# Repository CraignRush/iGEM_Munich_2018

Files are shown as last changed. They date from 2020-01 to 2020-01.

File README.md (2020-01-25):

# iGEM Munich 2018 Repository
This is an additional repository for many files which were created during the 2018 iGEM Munich season. It consists of three parts:
- _PhageCAD:_ Some CAD files to 3D-Print phage models
- _DropletVaporizer:_ CAD files to build an easy droplet vaporizer to produce alginate beads (in our case with phages in it) via 3D-printing
- _Model:_ Some parts of the iGEM Munich 2018 model. A simulation, how phages would reproduce inside a cell with respect to degradation an other intrinsic processes

## PhageCAD

The phage model looks like this:
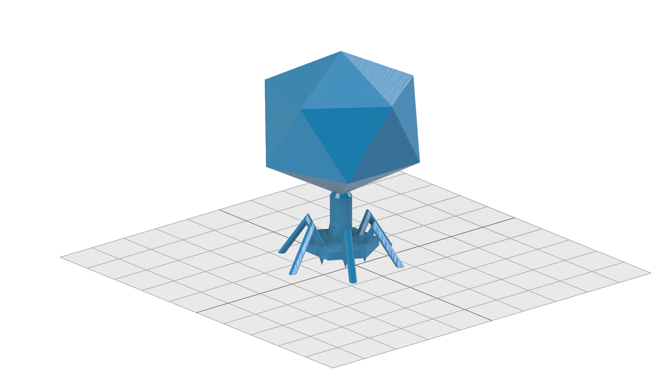
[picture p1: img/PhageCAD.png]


## Droplet Vaporizer
### Introduction

Phactory yields phages with toxicity levels that allow for oral administration to the patient. However, oral delivery requires protection of the phages from rapid degradation in the acidic gastric juice, while direct intravenous application requires additional purification steps. To overcome these hurdles, we prototyped two 3D-printed fluidic devices that each can be assembled for less than $5.

For oral application, we built the Phagecapsulator, a nozzle to encapsulate the phages in monodisperse calcium-alginate microspheres that protect them in the stomach. For intravenous administration, we can purify the bacteriophages from the remaining cell-extract via fractionation in a pressure-driven size-exclusion Phactory-Purificator filter system.

### Phage-Encapsulator
#### Motivation

As in many manufacturing processes, packaging of our produced phages is the final step of Phactory. Packaging provides long-term storability and ensures a clean and safe product for patients. Lacking access to commercial bioencapsulation devices such as the Inotech Encapsulator IER-50, available at $10,000, we engineered Phage-Encapsulator, an affordable device for encapsulating phages in monodisperse alginate spheres (1).

Requiring only standard parts, phage solution, alginate and compressed air, Phage-Encapsulator makes phage packaging accessible to non-specialized laboratories. The throughput is sufficient to produce encapsulated phages for oral application on-site in less than 2 hours.
Overall design

The core part of the Phage-Encapsulator consists of a dispensing tip that is continuously fed with phage containing alginate solution by a syringe pump. The dispensing tip is surrounded by a chamber connected to a compressed air supply to create a steady stream of air around the tip that shears off a jet of monodisperse droplets, smaller than the diameter of the tip. The alginate droplets are sprayed into a Calcium-Chloride bath where the rapid crosslinking reaction occurs.

<p align="center">
  A generic square placeholder image with ounded corners in a figure. 
  A generic square placeholder image with rounded corners in a figure.
 
</p>

#### Individual Parts:
##### Alginate Solution

The negatively charged polysaccharide alginate is commonly used for cell encapsulation or as food additive. Alginate undergoes strong shrinking when the pH of the environment drops below its pKa (2). Due to its pKa of ~3.5 this is the case in gastric fluid with a pH of 1 – 2. These properties render alginate spheres an ideal delivery substrate, protecting the phages in the stomach and releasing them in the basic milieu of the intestinal tract. As a tradeoff between alginate viscosity and gel strength, we found that a mixture of 1.8% high viscosity alginate (Art.-No. 9180.1, ROTH) and 0.2 low viscosity alginate (A1112, Sigma Aldrich) represents a good compromise.

##### Nozzle
Our final design of the nozzle is shown in Interactive Figure 1. It consists of a chamber that can be connected to a pressure supply via a universial tube adapter. Consisting of two parts, the nozzle does not get in contact with the phage solution, so it can be reused. The dispensing tip can be easily inserted via a Luer-lock adapter and lines up precisely with the nozzle orifice. A centering aid is located behind the orifice to reduce variances in cannula alignment, while the air stream is not disturbed unequally by its symmetric shape. At a given air pressure, the orifice diameter determines the velocity of the air stream and consequently the droplet diameter.

##### Calcium bath
Rapid gelation of the phage-containing alginate droplets was obtained in a 10 mM MgSO4 solution with 1.8% CaCl2. Aggregation of alginate droplets was prevented by continuous stirring during droplet generation with a magnet stirrer.

##### Syringe pump
In our experiments we used a commercial syringe pump from TSE Systems (type 540060) to create a continuous alginate stream. We designed our nozzle to be compatible with other types of syringe pumps, including open-source solutions.

##### Pressure supply
As a pressure supply we used the house gas line, reduced to 1 bar. If not available, the universial tube adapter ensures compatibility to alternative pressure supplies, including portable, open-source solutions.
Part List

- syringe (1ml Braun Omnifix)
- dispensing Tip (ID 0.51mm, Vieweg)
- syringe pump
- pressure supply
- pneumatic tubing
- 4x M3x20 screws + nuts
- 3D printed nozzle (PMMA)

#### Results

Our results show that after 1 hour incubation in simulated gastric fluid, active phages are successfully released in simulated intestinal fluid. Within the limited time frame of the iGEM competition we were able to show storability of these alginate spheres with constant phage activity at 4°C for four weeks, while stability for several months was shown in the literature (3).

##### Droplets are Monodisperse
<p align="center">
  
  <br>
  <p align="center">
    Alginate composition of 1.8 % Alginate and<br>0.2 % low-viscosity Alginate delivers<br>spherical Alginate microspheres.
  </p>
</p>
<br>
<p align="center">
  
  <br>
  <p align="center"  width="40%">
    Alginate encapsulated phages, DNA stained with SYBR Gold.
  </p>
</p> 
In order to achieve defined phage concentrations and therefore defined doses, we optimized the monodispersity of our alginate droplets.

In our initial attempts to create alginate droplets the size within a batch often varied significantly. Additionally, due to aggregation a lot of droplets were lost. Optimization of parameters such as flow rate, alginate concentration and N2 pressure led to an increase of monodispersity for all tested sizes (50-300 μm). Specifically, an alginate concentration of 1.8 % alginate and 0.2 % low-viscosity alginate proved to be ideal. Pressure and flow rate determine the droplet sizes.
<p align="center">

 <br>
 <p align="center">Monodispersity of alginate droplets with three different diameters<br>before and after optimization of the hardware device.</p>
 </p>

##### Bacteriophages Encapsulated In Alginate Can Withstand Gastric Acid 

The main problem of oral application is the acidic environment in the gastric fluid, necessitating protective measures against degradation. The other requirement of phage protection is the release of functional phages in the intestines. For this reason we compared the behavior of the encapsulated phages and non-encapsulated phages in simulated gastric fluid (SGF) and simulated intenstinal fluid (SIF).

In SGF, the number of active non-encapsulated phages decreases by more than 99.99 % within an hour. This shows the urgent need of a form of protection against degradation to make oral application of bacteriophages possible. As a reference, we used phages that were chemically released by citrate from alginate droplets.
<p align="center">

 <br>
 <p align="center">Non-encapsulated phages are highly degraded<br>within an hour in simulated gastric fluid.</p>
</p>

In comparison, the encapsulated phages were tested in SGF for the same time as the non-encapsulated phages. Afterwards, the same droplets were exposed for two hours to simulated intestinal fluid to test the release of functional bacteriophages in this environment.

The encapsulated phages were barely released in an hour of exposure to SGF. After transfering the capsules to SIF the number of active phages reached that of the undegraded reference. This indicates that the encapsulation of bacteriophages in alginate capsules enables the possibility of an oral application. Further experiments could test the alginate capsules in an animal model system.
<p  align="center">

 <br>
 <p align="center" >A small amount of encapsulated phages are released in SGF.<br> In SIF, functional phages are released in high concentration.</p>
 </p>

### References
<ol>
<li> <a href=https://doi.org/10.1016/j.biomaterials.2009.07.034>Chan, A. W., &amp; Neufeld, R. J. (2009). Modeling the controllable pH-responsive swelling and pore size of networked alginate based biomaterials. Biomaterials, 30(30), 6119–6129. </a></li>
<li> <a href=https://doi.org/10.1016/j.ab.2007.10.045>Kwon, Y.-C., Hahn, G.-H., Huh, K. M., &amp; Kim, D.-M. (2008). Synthesis of functional proteins using Escherichia coli extract entrapped in calcium alginate microbeads. Analytical Biochemistry, 373(2), 192–196. </a></li>
<li> <a href=https://doi.org/10.1038/srep41441>Colom, J., Cano-Sarabia, M., Otero, J., Aríñez-Soriano, J., Cortés, P., Maspoch, D., &amp; Llagostera, M. (2017). Microencapsulation with alginate/CaCO3: A strategy for improved phage therapy. Scientific Reports, 7(1). </a></li>
</ol>

## Model

Visit this page for more information regarding the model.
### Cell-free Biosynthesis of Bacteriophages

The seemingly simple experimental procedures of the optimized framework of Phactory may lead to the false impression that cell-free biosynthesis of bacteriophages is a trivial process. In fact, the production of phages represents one of the most complicated self-assembly processes that have been realized in a synthetic context.

We chose the T7 phage as a model system for cell-free phage production, because it is well characterized in the literature and our experiments. The phage assembly reaction resembles a temporally orchestrated process, which involves the expression of more than 40 proteins. This genetic program, encoded by the phage genome, is executed in a test tube containing hundreds of proteins, ribosomes, tRNAs and small molecules.

Due to the complexity of this process, variations in the quality of our cell extract cause irreproducible results. To optimize bacteriophage titers, we created a model based on ordinary differential equations to understand the essential features of a phage assembly reaction in a quantitative manner.

### Assumptions and Parameter Estimation

A phage assembly reaction follows a temporal program (1). First, the genes controlled by E. coli promoters, including the T7 DNA and RNA polymerase are expressed. Once the T7 RNA polymerase is present, the transcription of genes under a T7 promoter, e.g. the capsid proteins, starts. Our experiments revealed that simultaneously the phage genome being is replicated by the T7 DNA polymerase. As soon as a sufficient amount of capsid proteins is produced, they self-assemble to form empty phage capsids. In a final step the phage genome is packed into the empty capsids forming functional phages. In the following paragraphs we develop a set of ordinary differential equations that describe the phage assembly reaction, give analytical results where appropriate and estimate realistic reaction rate constants.

The modelled properties can be shown by the following tree diagram:


The complete set of model equations is shown below. 
#### Reaction Fluxes
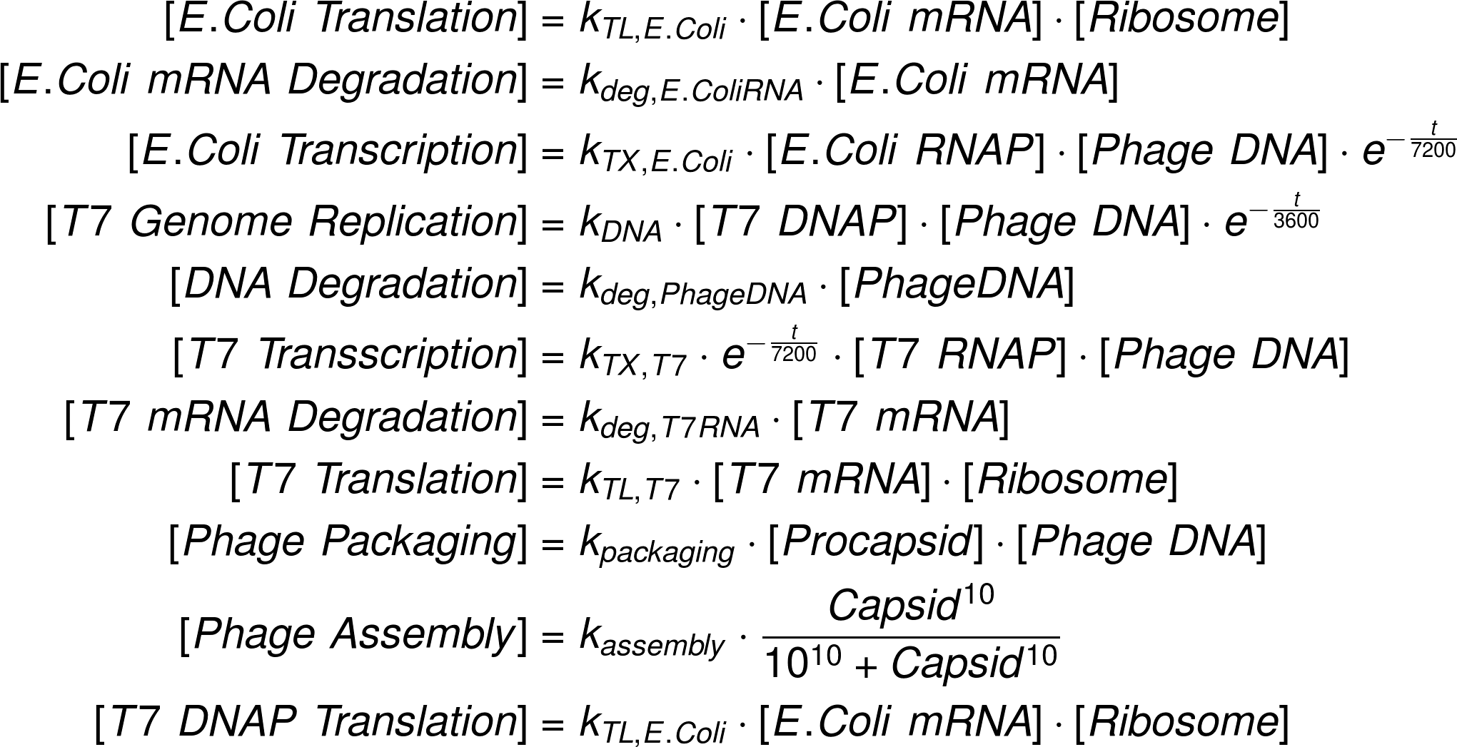
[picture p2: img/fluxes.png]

#### Ordinary Differential Equation System
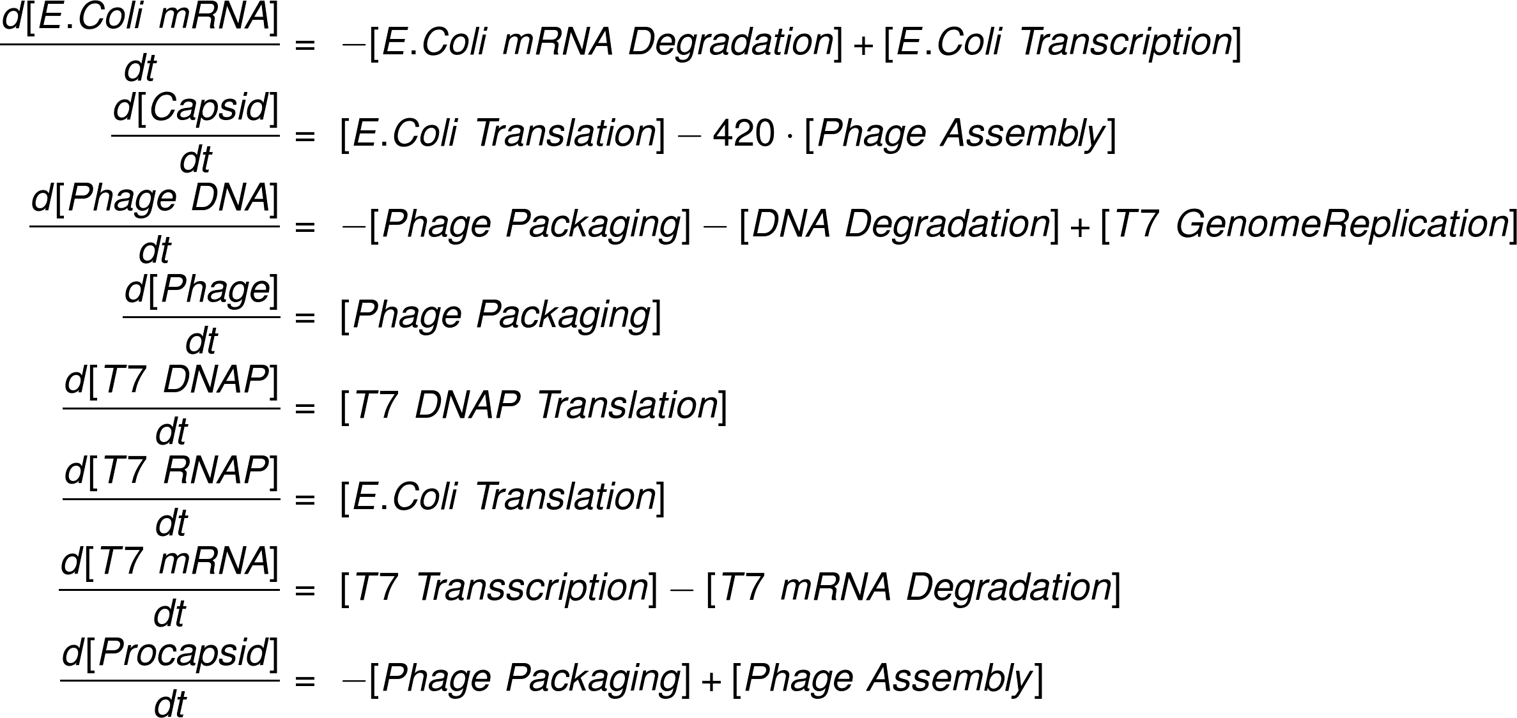
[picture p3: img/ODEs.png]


### Results

We used the MATLAB SimBiology toolbox to analyze the reactions numerically.

#### Phage Assembly Follows a Temporal Program

Evaluating our ODE model we can now follow the time traces of each reaction species in our system. Looking at the mRNA levels, it becomes evident that mRNA transcribed by E. coli RNA polymerase is produced instantly and rapidly reaches a low steady-state level. mRNA transcribed by the T7 RNA polymerase is produced after a time delay and reaches a much higher steady-state level, consistent with the faster transcription rate. Both mRNA levels decrease as the steady state level decreases due to the finite lifetime of the cell extract.

Following protein levels, we see that production of the T7 DNA and RNA polymerases starts first, while production of the T7 RNA polymerase controlled capsid proteins sets in later. When the free capsid proteins exceed the critical concentration __K<sub>c</sub>__ , they start to be assembled into full capsids and the free capsid protein concentration approaches a steady-state. All protein levels approach a final level at the end of the reaction.
<p align="center">

 <br>
 <p align="center">mRNA levels over time in the cell-extract.<br>before and after optimization of the hardware device.</p>
 </p>

Further, it is instructive to inspect the time traces of free DNA and fully packed active phages. As soon as sufficient T7 DNA polymerase is present, the phage genomes are being amplified to approximately 10 times the initial level. The assembly and packing of functional phages, however, only kicks in after an initial time delay. Importantly, this allows the genome to be freely transcribed and replicated, before the negative feedback introduced by DNA packing, impedes further phage production.
<p align="center">

 <br>
 <p align="center">T7 polymerase generation by the E.coli in-house polymerase</p>
 </p>

<p align="center">

 <br>
 <p align="center">Phage production and DNA levels over time</p>
 </p>

#### DNA Stability

To analyze the influence of DNA stability, we screened a range of DNA degradation rates as shown in the figure on the right. Phages are produced until a critical degradation rate of __&delta;<sub>g,c</sub> &asymp; 2 &sdot; 10<sup>-4</sup>__ is reached. This results in lower concentrations of proteins in downstream reactions and resultingly prohibits the formation of procapsids.
<p align="center">

 <br>
 <p align="center">Influence of DNA degradation on the phage production</p>
 </p>

#### Impact of Positive Feedback via DNA Replication

To evaluate the influence of the positive feedback loop introduced by DNA replication, we conducted experiments with and without addition of dNTPs to the reaction mixture. With our model we can simulate this experiment by setting the DNA replication rate to zero.

The bar plot on the right shows enhanced phage packaging of over one decade by the integrated feedback loop of the T7 DNA polymerase.
 
 <p align="center">

 <br>
 <p align="center">Evaluation of DNA polymerase in the phage production.</p>
 </p>

### Conclusions

Based on the results, we identified that enhancing DNA stability and maximizing protein yield are the most relevant parameters to improve phage titers. After optimizing our protocols accordingly, we reached __10<sup>7</sup>__ phages per __10 µL__ reaction - sufficient to treat up to 10 patients.

### References
<ol>
<li id="ref_1"> <a href=https://pubs.acs.org/doi/abs/10.1021/sb300049p>  Shin, J., Jardine, P., &amp; Noireaux, V. (2012). Genome Replication, Synthesis, and Assembly of the Bacteriophage T7 in a Single Cell-Free Reaction. ACS Synthetic Biology, 1(9), 408–413.</a></li>
<li id="ref_2"> <a href=https://www.jove.com/video/56144/synthesis-infectious-bacteriophages-an-e-coli-based-cell-free>  Rustad, M., Eastlund, A., Marshall, R., Jardine, P., &amp; Noireaux, V. (2017). Synthesis of infectious bacteriophages in an E. coli-based cell-free expression system.
</a></li>
<li id="ref_3"> <a href=https://doi.org/10.1103/PhysRevLett.106.048104>  Karzbrun, E., Shin, J., Bar-Ziv, R. H., &amp; Noireaux, V. (2011). Coarse-grained dynamics of protein synthesis in a cell-free system. Physical Review Letters, 106(4).</a></li>
<li id="ref_4"> <a href=https://doi.org/10.1021/sb400203p>Siegal-Gaskins, D., Tuza, Z. A., Kim, J., Noireaux, V., &amp; Murray, R. M. (2014). Gene Circuit Performance Characterization and Resource Usage in a Cell-Free “Breadboard.” ACS Synthetic Biology, 3(6), 416–425. </a></li>
<li id="ref_5"> <a href=https://doi.org/10.1021/sb400131a>
Sun, Z. Z., Yeung, E., Hayes, C. A., Noireaux, V., &amp; Murray, R. M. (2014). Linear DNA for rapid prototyping of synthetic biological circuits in an Escherichia coli based TX-TL cell-free system. ACS Synthetic Biology, 3(6), 387–397.  </a></li>

<li id="ref_6"> <a href=http://www.jbc.org/content/286/1/234.full>Ionel, A., Velázquez-Muriel, J. A., Luque, D., Cuervo, A., Castón, J. R., Valpuesta, J. M., … Carrascosa, J. L. (2011). Molecular Rearrangements Involved in the Capsid Shell Maturation of Bacteriophage T7. Journal of Biological Chemistry, 286(1), 234–242. </a></li>
<li id="ref_7"> <a href=https://books.google.de/books?hl=de&amp;lr=&amp;id=vgyBJbtNOcoC&amp;oi=fnd&amp;pg=PP1&amp;dq=israelachvili&amp;ots=_PQtchA1Q9&amp;sig=Bw7OdRovpmTt5FKFaZCesKrPM18#v=onepage&amp;q=israelachvili&amp;f=false>Israelachvili, J. N. (2011). Intermolecular and surface forces. Academic press.</a></li>

</ol>

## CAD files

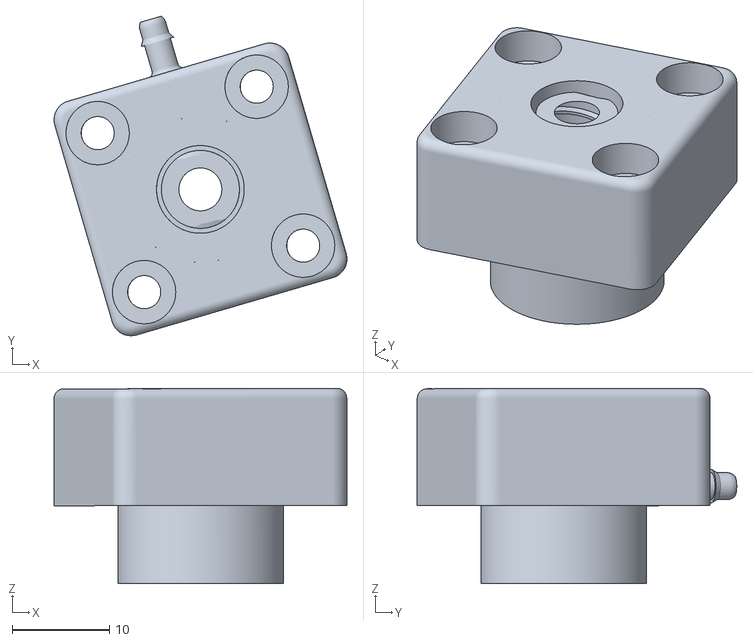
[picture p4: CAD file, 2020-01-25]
DropletVaporizer/Baugruppe_Zerstäuber_Top_V2.stl
30.1 x 32.8 x 20.0

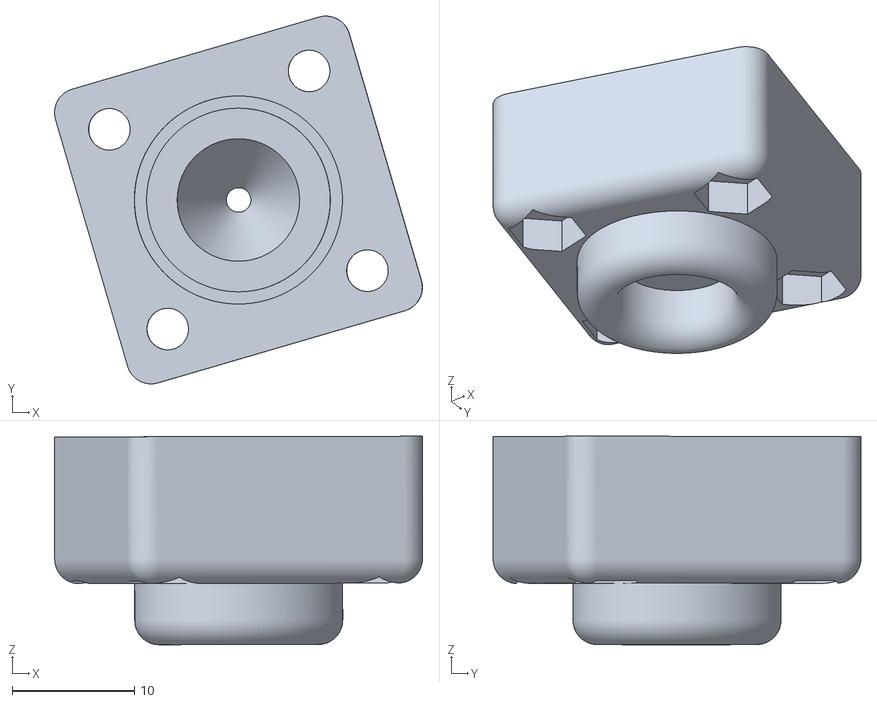
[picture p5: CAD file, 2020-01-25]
DropletVaporizer/Baugruppe_Zerstäuber_Bottom_V2.stl
30.1 x 30.0 x 17.0

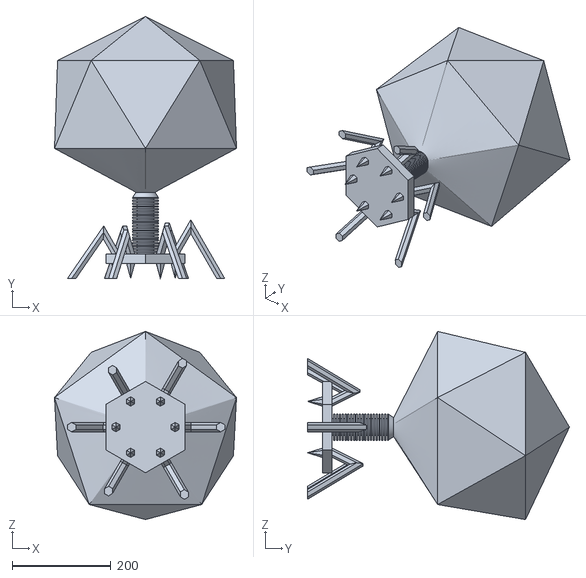
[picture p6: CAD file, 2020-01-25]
PhageCAD/Bacteriophage.stl
368.4 x 530.3 x 380.8

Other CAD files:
DropletVaporizer/Baugruppe_Zerstäuber.iam
DropletVaporizer/Oberteil_Zerstäuber.ipt
DropletVaporizer/Oberteil_Zerstäuber_MIR.ipt
DropletVaporizer/Unterteil_Zerstäuber.ipt
DropletVaporizer/Zerstäuber_Luer_Lock.ipt
PhageCAD/Bacteriophage.ipt
PhageCAD/Phage_Assembly.iam
PhageCAD/Phage_Assembly_3.iam
PhageCAD/Phage_Hat.ipt

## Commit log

2020-01-25 Folder structure change
    [Bacteriophage.ipt, Bacteriophage.stl, Baugruppe_Filter.ipn, Baugruppe_Zerstäuber.iam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]
2020-01-25 Added phage image
    [Phage.ipn]
